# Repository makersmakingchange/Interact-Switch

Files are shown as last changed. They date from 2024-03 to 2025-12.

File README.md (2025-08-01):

 # Interact Switch
<!---  SUMMARY A brief summary of the project. What it does, who it is for, how much it costs. --->

The Interact Switch is an open source assistive switch. The switch is comprised of 3D printed parts and off-the-shelf electronics. The Interact Switch is a high quality, modular 3D printable switch design. The tactile feel of the switch is on par with commercial switches, coming in at about 35 gf of activation force across the surface of the switch. The base has the same footprint as a Jellybean switch, and should work with any Jellybean switch mounts.

There are a wide array of different designs: from a simple flat button, to textured designs, to a dome, and even some wobble switch variants.

The switch base incorporates 6 slots that are ideal for a variety of mounting options, including using hook and loop straps (e.g., VELCRO). The overall cost of materials is about $8 (plus $8 for component shipping).

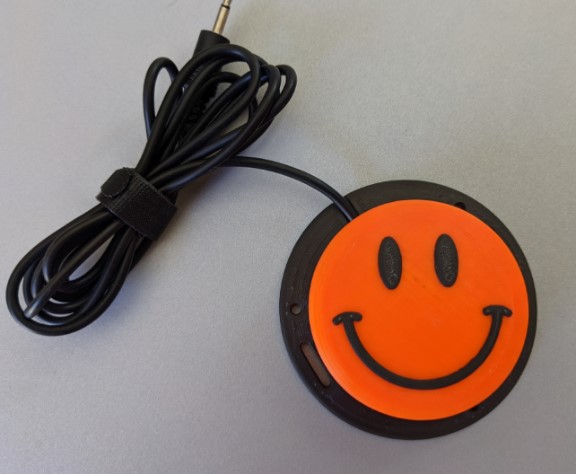
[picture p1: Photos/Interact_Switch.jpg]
A 3D printed Interact Switch with smiley topper


## More info at
- [Makers Making Change Library Page](https://www.makersmakingchange.com/s/product/interact-switch/01tJR000000698vYAA)

## How to Obtain the Device
### 1. Do-it-Yourself (DIY) or Do-it-Together (DIT)

This is an open-source assistive technology, so anyone is free to build it. All of the files and instructions required to build the device are contained within this repository. Refer to the Maker Guide below.

### 2. Request a build of this device

You may also submit a build request through the [MMC Library Page](https://www.makersmakingchange.com/s/product/interact-switch/01tJR000000698vYAA) to have a volunteer maker build the device. As the requestor, you are responsible for reimbursing the maker for the cost of materials and any shipping.

### 3. Build this device for someone else

If you have the skills and equipment to build this device, and would like to donate your time to create the device for someone who needs it, visit the [MMC Maker Wanted](https://makersmakingchange.com/maker-wanted/) section.

## Build Instructions

### 1. Read through the Maker Guide

The Maker Guide  [EN](/Documentation/Interact_Switch_Maker_Guide.pdf), WIP <!---([FR](/Documentation/FR_Interact_Switch_Maker_Guide.pdf)) --->  contains all the necessary information to build this device, including tool lists, assembly instructions, programming instructions (if applicable) and testing.

### 2. Order the Off-The-Shelf Components

The [Bill of Materials](/Documentation/Interact_Switch_BOM.csv) lists all of the parts and components required to build the Interact Switch. The main switch component needs to be ordered online. The rest of the off-the-shelf components are also online or may be available in smaller quantities at your local hardware store or dollar store.

### 3. Print the 3D Printable components

All of the individual print files can be found in the [/Build_Files/3D_Printing_Files](/Build_Files/3D_Printing_Files/) folder.

### 4. Assemble the <Device-Name>

Reference the Assembly Guide([EN](/Documentation/Interact_Switch_Maker_Guide.pdf),[FR](/Documentation/FR_Interact_Switch_Assembly_Guide.pdf)) for the tools and steps required to build each portion.

## How to improve this Device
As open source assistive technology, you are welcomed and encouraged to improve upon the design. 

## Files
### Documentation
| Document             | Version | Link |
|----------------------|---------|------|
| Design Rationale     | 2.0     | [Interact_Switch_Design_Rationale](/Documentation/Interact_Switch_Design_Rationale.pdf)    |
| Maker Guide          | 2.0     | [Interact_Switch_Maker_Checklist](/Documentation/Interact_Switch_Maker_Guide.pdf)          |
| Topper Guide         | 2.0     | [Interact Switch Topper Guide](/Documentation/Interact_Switch_Topper_Guide.pdf)            |
| Bill of Materials    | 2.0     | [Interact_Switch_Bill_of_Materials](/Documentation/Interact_Switch_BOM.csv)                |
| User Guide           | 2.0     | [Interact_Switch_User_Guide](/Documentation/Interact_Switch_Quick_Guide.pdf)               |
| Changelog            | 2.0     | [Interact_Switch_Changelog](CHANGES.txt)     |

### Design Files
<!--- DESIGN FILES If possible, include a copy of original design files to facilitate easy editing and customization. --->
 - [CAD Files](/Design_Files/CAD_Design_Files)

### Build Files
 - [3D Printing Files](/Build_Files/3D_Printing_Files)

## Attribution
The [original design](https://github.com/mwturvey/InteractSwitch) of the Interact Switch was by Mike Turvey.

Modifications to the design and additional documentation by Neil Squire Society / Makers Making Change.
  - Increases the screw hole size in the ButtonCapHolder to accept #4 3/8" screws instead of M2.5 screws.
  - Lines up the holes in the base with the holes in the ButtonCapHolder.
  - Deepens the countersink in the Base for the screws.
  - Removes the need for supports on the Base piece.
  - Decreases the required sanding by tapering the tabs on the ButtonCapHolder.  

Because of the modifications made to the base and button cap holder to accomodate the #4 screws, they are no longer backwards compatible with the original files and is not longer compatible with M2.5 screws.

### Contributors
 - Mike Turvey
 - Stephen Moyer. Neil Squire Society.
 - Brad Wellington. Neil Squire Society.
 - Jake McIvor. Neil Squire Society.
---

<!-- ABOUT MMC START -->
## About Makers Making Change
[Makers Making Change Logo](https://www.makersmakingchange.com/)

Makers Making Change is a program of [Neil Squire](https://www.neilsquire.ca/), a Canadian non-profit that uses technology, knowledge, and passion to empower people with disabilities.

Makers Making Change leverages the capacity of community based Makers, Disability Professionals and Volunteers to develop and deliver affordable Open Source Assistive Technologies.

 - Website: [www.MakersMakingChange.com](https://www.makersmakingchange.com/)
 - GitHub: [makersmakingchange](https://github.com/makersmakingchange)
 - Bluesky: [@makersmakingchange.bsky.social](https://bsky.app/profile/makersmakingchange.bsky.social)
 - Instagram: [@makersmakingchange](https://www.instagram.com/makersmakingchange)
 - Facebook: [makersmakechange](https://www.facebook.com/makersmakechange)
 - LinkedIn: [Neil Squire Society](https://www.linkedin.com/company/neil-squire-society/)
 - Thingiverse: [makersmakingchange](https://www.thingiverse.com/makersmakingchange/about)
 - Printables: [MakersMakingChange](https://www.printables.com/@MakersMakingChange)

### Contact Us
For technical questions, to get involved, or to share your experience we encourage you to [visit our website](https://www.makersmakingchange.com/) or [contact us](https://www.makersmakingchange.com/s/contact).
<!-- ABOUT MMC END -->

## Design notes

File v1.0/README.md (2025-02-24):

Edit: This quick fix to the design incorporates the following:
- Increases the screw hole size in the ButtonCapHolder to accept both M2.5 screws as well as #4 3/8" screws.
- Lines up the holes in the base with the holes in the ButtonCapHolder.
- Deepens the countersink in the Base for the screws.
- Removes the need for supports on the Base piece.
- Decreases the required sanding by tapering the tabs on the ButtonCapHolder.

Note: Only the generic ButtonBase has been updated, not the ButtonBase_Spade.

# InteractSwitch
Designs for a set of assistive technology switches

You can read more about the development of this switch here, as well as see a bunch of pictures & comments: https://cdn.thingiverse.com/assets/da/2f/63/38/8b/card_preview_newButton2.PNG

Build instructions can be found here:

https://docs.google.com/document/d/1uWRKXmApZUaSo1I0oyyFrAfncziYsd2_8ai8dunogJs/edit?usp=sharing

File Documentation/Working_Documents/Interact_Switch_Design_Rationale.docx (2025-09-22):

# Overview

The Design Rationale is intended to provide designers and maker information about the design process and design decisions behind the development of the Interact Switch, a customizable assistive switch with a large activation area.

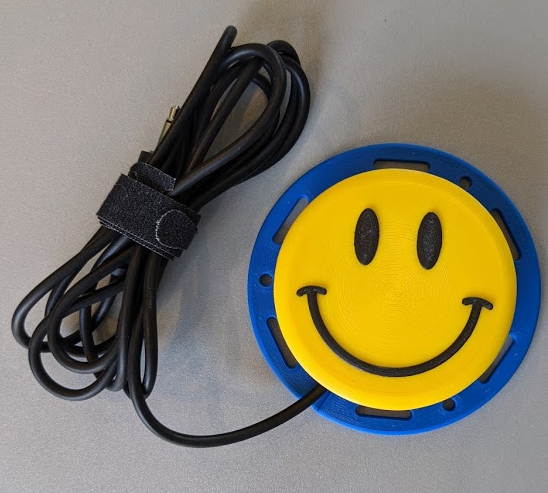
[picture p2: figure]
an interact switch with a smiley face

# Introduction

The original design for the Interact Switch came from the design by Mark Turvey. (https://github.com/mwturvey/InteractSwitch)

# Detailed Design

## Initial Changes

The initial changes made to the original design were

- Increases the screw hole size in the ButtonCapHolder to accept both M2.5 screws as well as #4 3/8" screws.
- Lines up the holes in the base with the holes in the ButtonCapHolder.
- Deepens the countersink in the Base for the screws.
- Removes the need for supports on the Base piece.
- Decreases the required sanding by tapering the tabs on the ButtonCapHolder.

## Improvements over time

Further changes were made over time to the following components

### Base

#### Cable Routing

Changes were made to the cable routing path to make the cable align better to the position of the switch

#### Button Cap

#### Upside Down Print Issues

The filets and arcs on the bottom of the button cap caused print quality issues with bridging when printed upside down. For the textured caps this was not a large issue since it was not printed upside down, but did pose an issue for the plain cap. The arcs and filets were replaced with a straight line to improve the bridging when printed upside down.

### Button Cap Holder

#### Screw Insertion

When assembling the device, some users were having trouble aligning the screw with the holes in the Button Cap Holder, and the screws would sometimes screw into the wall of the holder instead of the hole.

A 0.6mm chamfer was added to the hole to catch and guide the screw into the hole.

#### Screw Torque

When using the #4 sheet metal screw, the torque required to tighten the screw broke some of the holders. The hole was loosened to 3.0mm to get a much better tightening torque, but this makes the base and the cap holder no longer backwards compatible with the original, as it no longer works with M2.5 screws.

## File Update

CAD files were updated and rebuilt into one central file. This corrected several minor errors, such as the screw holes on the base and the screw holes on the cap holder being misaligned by 0.5mm, as well as making heavy use of parameters. Because of this rebuild, changes can be made to one parameter, and the changes will propagate out to all connected parts.

## Soldering Jig

An opportunity for improvement for the Interact Switch that was identified was the creation of a soldering jig to prevent makers from soldering to the wrong terminals on the switch, and to prevent large blobs of solder that would make assembly difficult. After 4 iterations, a soldering jig was created that held the switch at a 90 degree angle to the cable, covers the wrong terminal, and holds the cable in place without tipping.

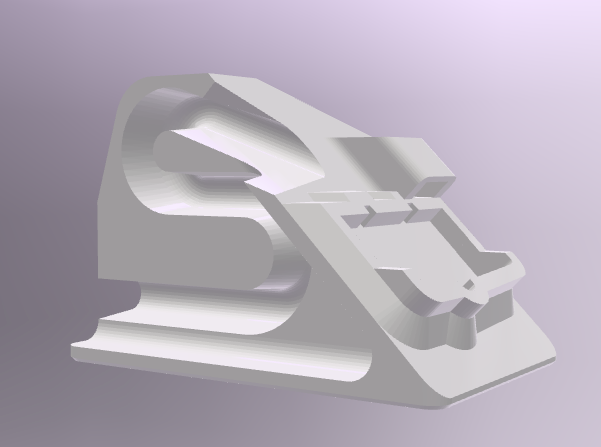
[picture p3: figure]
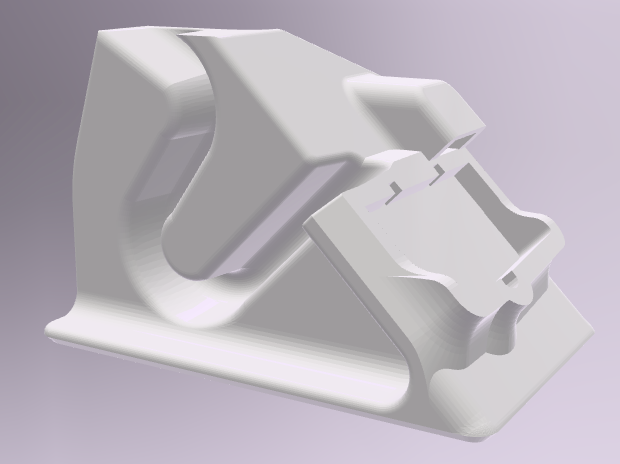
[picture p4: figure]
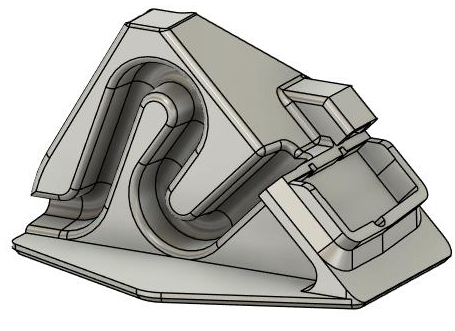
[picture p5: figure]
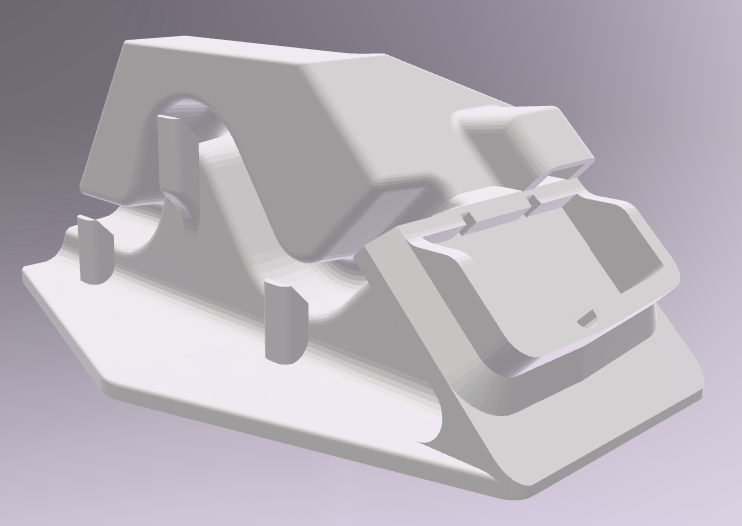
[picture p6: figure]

# Opportunities for Improvement

There are further opportunities for improvement that have been identified

- Better indicate the orientation of the switch when assembling the device
- Clarify how to use the base as a soldering jig
- Change the shape of the button cap for better bridging

© 2025 by Neil Squire. This work is licensed under the CC BY SA 4.0 License: http://creativecommons.org/licenses/by-sa/4.0 Files available at https://github.com/makersmakingchange/Interact-Switch Page 1 of 1

V2.0 | July 2025 Interact Switch Design Rationale

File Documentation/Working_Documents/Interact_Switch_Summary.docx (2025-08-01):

# Overview

The Device Summary is intended to be a detailed summary of the device, product and maker information for the Interact Switch, making it easier to add to the Makers Making Change website. It is intended for anyone who will view the device listing.

an interact switch with a smiley face

# Product Information

## Product Name

Interact Switch

## Device Category

Mark any relevant categories with an “X”:

| Adapted Toys
| Aids for Daily Living (ADL)
X | Assistive Switches
| Communication Aids (AAC)
| Computer Access
| Environmental Controls
| Gaming
| Keyguard
| Kits
| LipSyncs
| Mounting
| Recreation and Leisure
| Seating and Positioning
| Switch Interfaces
| Writing Aids

## User Value Statement

The Interact Switch is a high quality, modular 3D printable switch design. The tactile feel of the switch is on par with commercial switches, coming in at about 35 g of activation force across the surface of the switch. The base has the same footprint as a Jellybean switch, and should work with any Jellybean switch mounts.

## Designer

Original design by Mike Turvey (https://github.com/mwturvey/InteractSwitch)

Modifications to the design and additional documentation by Neil Squire Society / Makers Making Change.

# Device Information

## Overview

The Interact Switch is a high quality, modular 3D printable switch design. The tactile feel of the switch is on par with commercial switches, coming in at about 35 g of activation force across the surface of the switch. The base has the same footprint as a Jellybean switch and should work with any Jellybean switch mounts.

## Disability Type

Select one or more disability types and mark with an “X”:

| Agility / Dexterity
| Arthritis
X | Cognitive
| Hearing
X | Mobility
| Pain
| SCI
| Vision
| Other

## Disability Type Description

## The device is intended for users who have difficulty using small buttons or switches and need an accessible switch to operate them. This switch comes with different topper designs that can be 3D printed in contrasting colors which can be helpful to users with low vision.

## How To Use

The Interact Switch can be connected to any 3.5mm switch-compatible assistive device, such as the Xbox Adaptive Controller. Press the switch to activate the device. Since the device has the same footprint as a Jellybean switch, it is compatible with any Jellybean switch mounts. It can be placed on a flat surface, bolted in place, or secured with hook and loop (ex., Velcro) straps.

## Estimated Cost

The estimated material cost of the device for a single build:

X | $0 - $10
| $11 - $25
| $26 - $50
| $51 - $100
| $101 - $250
| $250+

## Attribution

Original Design by Mike Turvey

# Maker Information

## Project Skills

Mark the required project skills with an “X”:

X | 3D Printing
| Custom PCB
X | Electronics
| Laser Cutting
| Mechanics
| Software
X | Soldering
| Woodworking
| Other

## Skills Description

To build this device a maker needs to be able to 3D print and do basic soldering

## Tools Needed

X | 3D Printer
| Common Hand Tools
| Common Power Tools
| Laser Cutter
X | Soldering Iron
| Specialized Tooling

## Print time (hrs)

1hr8min

## Assembly time (hrs)

0hr10min

## Build Instructions

The parts are 3D printed and assembled with 3 screws. A mono cable is stripped and then soldered to the switch.

## Download Link

https://github.com/makersmakingchange/Interact-Switch/archive/refs/heads/main.zip

## Project Link

https://github.com/makersmakingchange/Interact-Switch

# License

BSD 2-Clause License

Copyright (c) 2020, Michael Turvey

All rights reserved.

Redistribution and use in source and binary forms, with or without

modification, are permitted provided that the following conditions are met:

1. Redistributions of source code must retain the above copyright notice, this

list of conditions and the following disclaimer.

2. Redistributions in binary form must reproduce the above copyright notice,

this list of conditions and the following disclaimer in the documentation

and/or other materials provided with the distribution.

THIS SOFTWARE IS PROVIDED BY THE COPYRIGHT HOLDERS AND CONTRIBUTORS "AS IS"

AND ANY EXPRESS OR IMPLIED WARRANTIES, INCLUDING, BUT NOT LIMITED TO, THE

IMPLIED WARRANTIES OF MERCHANTABILITY AND FITNESS FOR A PARTICULAR PURPOSE ARE

DISCLAIMED. IN NO EVENT SHALL THE COPYRIGHT HOLDER OR CONTRIBUTORS BE LIABLE

FOR ANY DIRECT, INDIRECT, INCIDENTAL, SPECIAL, EXEMPLARY, OR CONSEQUENTIAL

DAMAGES (INCLUDING, BUT NOT LIMITED TO, PROCUREMENT OF SUBSTITUTE GOODS OR

SERVICES; LOSS OF USE, DATA, OR PROFITS; OR BUSINESS INTERRUPTION) HOWEVER

CAUSED AND ON ANY THEORY OF LIABILITY, WHETHER IN CONTRACT, STRICT LIABILITY,

OR TORT (INCLUDING NEGLIGENCE OR OTHERWISE) ARISING IN ANY WAY OUT OF THE USE

OF THIS SOFTWARE, EVEN IF ADVISED OF THE POSSIBILITY OF SUCH DAMAGE.

© 2025 by Neil Squire. This work is licensed under the CC BY SA 4.0 License: http://creativecommons.org/licenses/by-sa/4.0 Page 1 of 2

V2.0 | July 2025 Interact Switch Summary

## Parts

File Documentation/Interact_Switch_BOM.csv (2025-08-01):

Device: | Interact Switch
Version: | V2.0
Last Updated: | 2025-07-08
 |  |  |  |  |  |  |  | Total filament (g) |  | Unit Cost | Total Estimated Cost | Build Cost
 |  |  |  |  |  |  |  | 35 |  | $8.70 | $8.70
ID | Commercial Parts |  |  |  |  |  |  |  |  | $7.82 | $7.82
 | Part | Description |  | Manufacturer | Supplier | QTY / Device | QTY / PKG | PKGs | $/ PKG | $ / Device | Total Estimated Cost |  | Link
 | Mono Cable |  |  |  | Digikey | 1 | 1 | 1 | $4.65 | $4.65 | $4.65 |  | https://www.digikey.ca/en/products/detail/tensility-international-corp/10-00344/2350247
 | Snap Action Switch |  |  |  | Digikey | 1 | 1 | 1 | $1.40 | $1.40 | $1.40 |  | https://www.digikey.ca/en/products/detail/omron-electronics-inc-emc-div/SS-3GP/664724
 | #4 Sheet Metal Screw |  |  |  | Digikey | 3 | 1 | 3 | $0.59 | $1.77 | $1.77 |  | https://www.digikey.ca/en/products/detail/serpac/6005/307599
 |  |  |  |  |  |  |  | 0 |  | $- | $-
 |  |  |  |  |  |  |  | 0 |  | $- | $-
 | 3D Printed Parts |  |  |  |  |  |  | 35 |  | $0.88 | $0.88
 | Part | Description | Filament Type | Filament | Color | QTY / Device | Mass (g) / Part | Total Mass | $ / kg | $ / Device | Total Estimated Cost |  | Link
 | Interact_Switch_Base |  | PLA |  | Any | 1 | 17 | 17 | $25.00 | $0.43 | $0.43
 | Interact_Switch_Cap_Plain |  | PLA |  | Any | 1 | 14 | 14 | $25.00 | $0.35 | $0.35
 | Interact_Switch_Holder |  | PLA |  | Any | 1 | 3 | 3 | $25.00 | $0.08 | $0.08
 | Interact_Switch_Insert_0.6mm |  | PLA |  | Any | 1 | 1 | 1 | $25.00 | $0.03 | $0.03
 |  |  |  |  |  |  |  | 0 |  | $- | $-
 |  |  |  |  |  |  |  | 0 |  | $- | $-
 |  |  |  |  |  |  |  | 0 |  | $- | $-
 |  |  |  |  |  |  |  | 0 |  | $- | $-

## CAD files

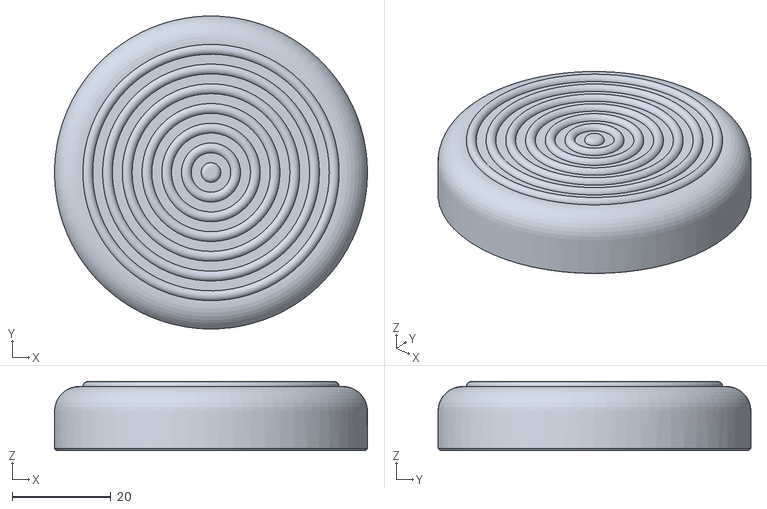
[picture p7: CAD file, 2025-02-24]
Build_Files/3D_Printing_Files/Alternate_Caps/ButtonCap_Rings.STL
63.5 x 63.5 x 14.0

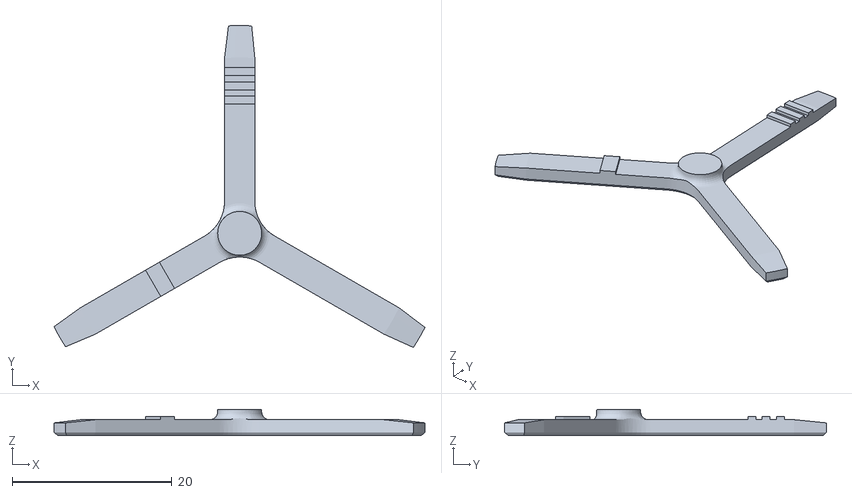
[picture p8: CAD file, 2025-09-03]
Build_Files/3D_Printing_Files/Alternate_Inserts/ButtonCapInsert_1.3mm.STL
46.4 x 40.3 x 3.30

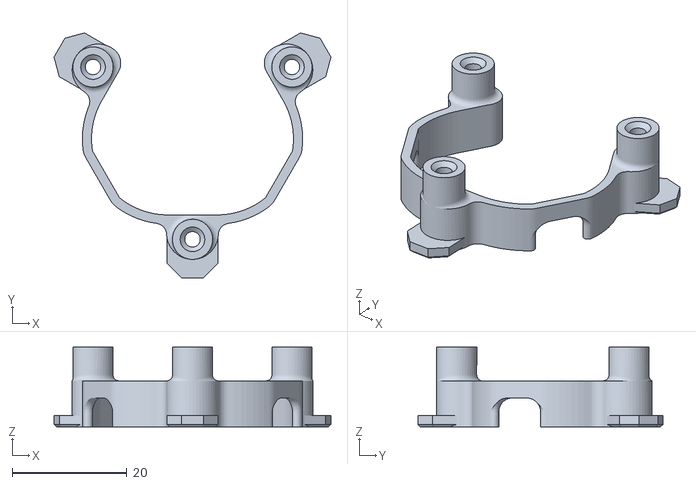
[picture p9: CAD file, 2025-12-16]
Build_Files/3D_Printing_Files/Interact_Switch_Holder.stl
48.2 x 42.7 x 13.9

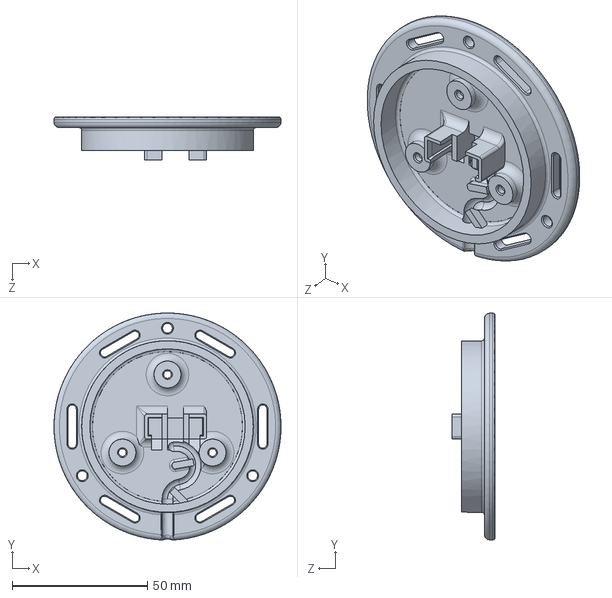
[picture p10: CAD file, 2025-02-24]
v1.0/sources/Base/ButtonBase_Spade.SLDPRT
84.0 x 84.0 x 16.0 mm

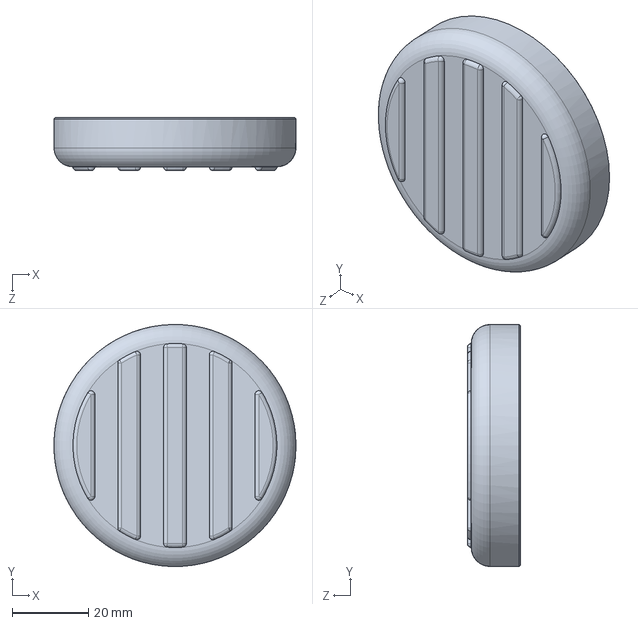
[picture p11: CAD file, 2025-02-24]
v1.0/sources/ButtonCap/ButtonCap_Lines_VeryWide.SLDPRT
63.5 x 63.5 x 14.0 mm

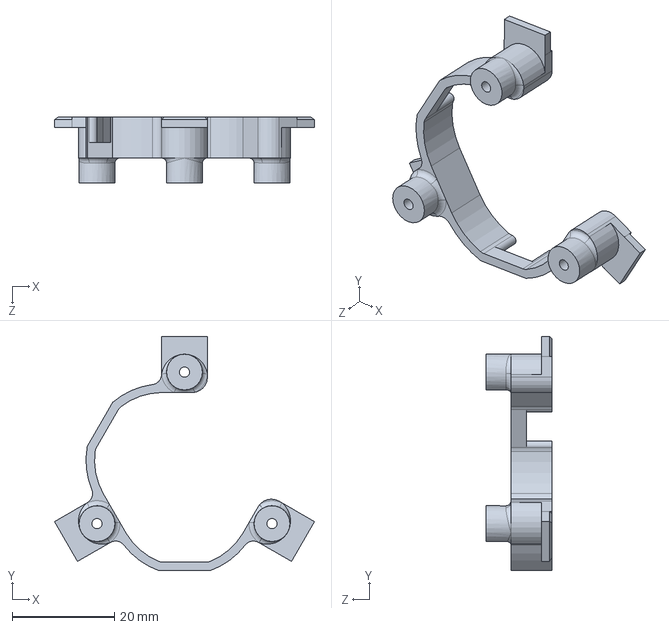
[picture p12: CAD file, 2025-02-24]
v1.0/sources/ButtonCapHolder/ButtonCapHolder.SLDPRT
50.8 x 45.8 x 12.8 mm

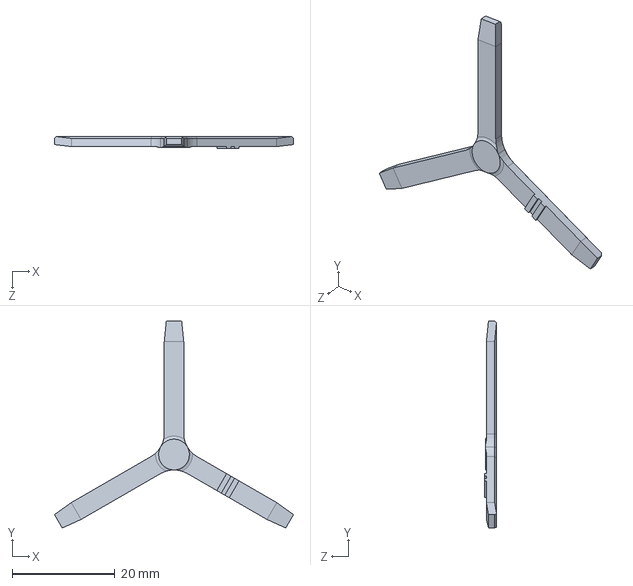
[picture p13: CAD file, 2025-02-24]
v1.0/sources/ButtonCapInsert/ButtonCapInsert_0.2mm.SLDPRT
46.5 x 40.3 x 2.40 mm

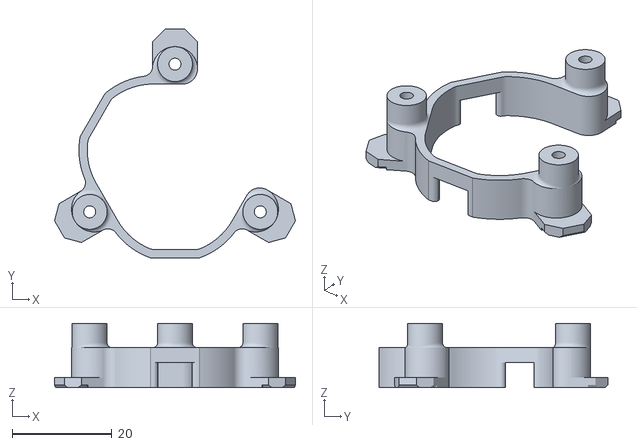
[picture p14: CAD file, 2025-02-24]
v1.0/stl/ButtonCapHolder/Quick Fix ButtonCapHolder.stl
48.3 x 45.8 x 12.9

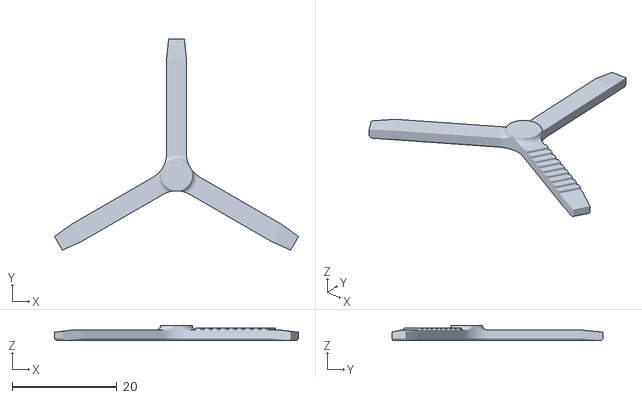
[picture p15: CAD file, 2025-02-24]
v1.0/stl/ButtonCapInsert/ButtonCapInsert_0.9mm.STL
46.5 x 40.3 x 2.90

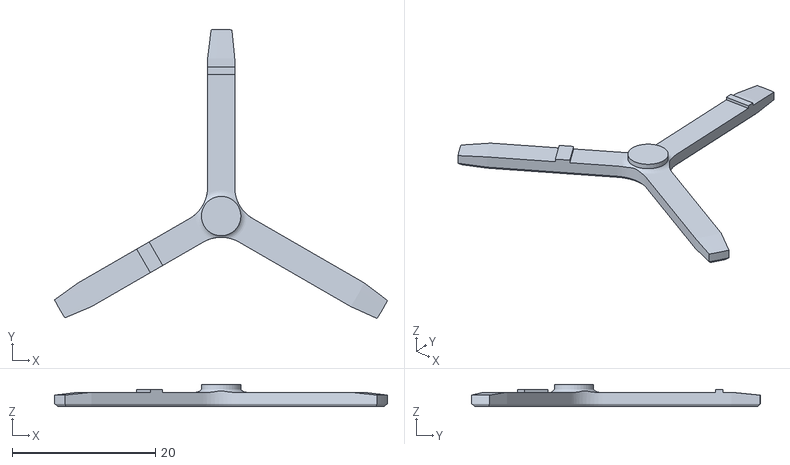
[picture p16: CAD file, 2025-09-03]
Build_Files/3D_Printing_Files/Alternate_Inserts/ButtonCapInsert_1.1mm.STL
46.4 x 40.3 x 3.10

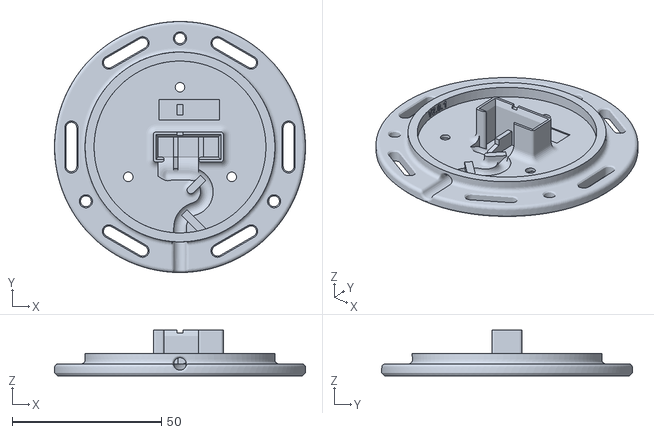
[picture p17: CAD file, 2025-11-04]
Build_Files/3D_Printing_Files/Interact_Switch_Base.stl
84.0 x 84.0 x 15.3

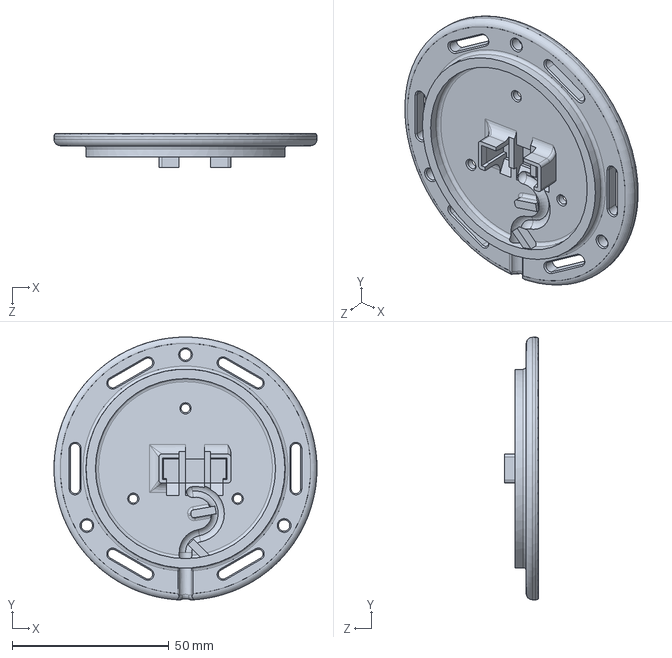
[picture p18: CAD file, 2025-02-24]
v1.0/sources/Base/ButtonBase.SLDPRT
84.0 x 84.0 x 11.0 mm

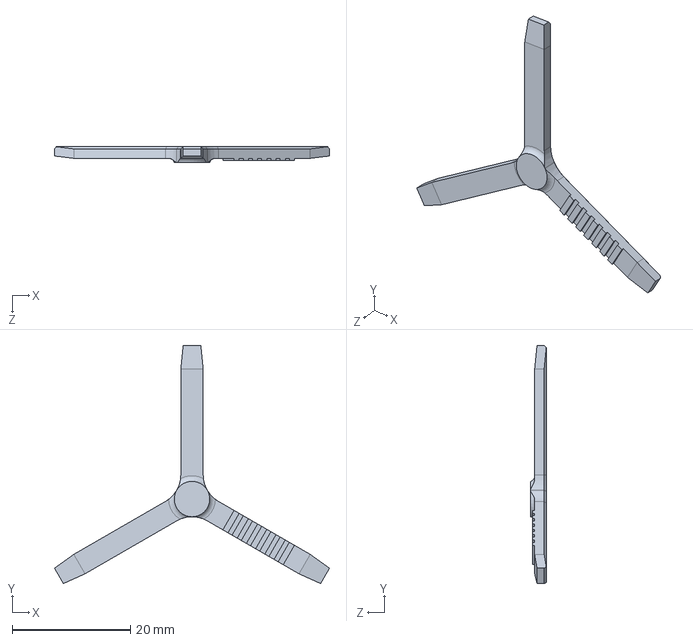
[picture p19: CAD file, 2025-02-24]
v1.0/sources/ButtonCapInsert/ButtonCapInsert_0.7mm.SLDPRT
46.5 x 40.3 x 2.70 mm

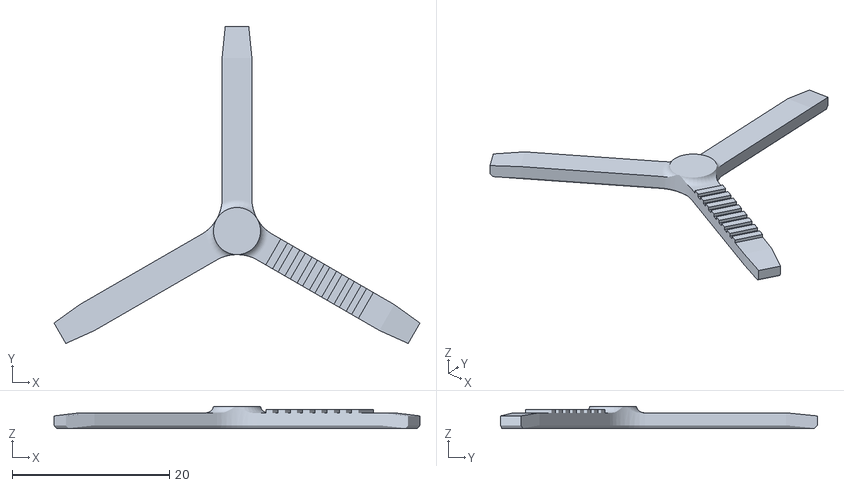
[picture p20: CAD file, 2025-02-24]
v1.0/stl/ButtonCapInsert/ButtonCapInsert_0.8mm.STL
46.5 x 40.3 x 2.80

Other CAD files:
v1.0/stl/Base/ButtonBase_Spade.STL
Build_Files/3D_Printing_Files/Alternate_Caps/ButtonCap_Lines_VeryWide.STL
v1.0/sources/ButtonCap/ButtonCap_Lines_Wide.SLDPRT
v1.0/stl/Base/Quick Fix ButtonBase.stl
Build_Files/3D_Printing_Files/Alternate_Caps/ButtonCap_Arrow.STL
Build_Files/3D_Printing_Files/Alternate_Caps/ButtonCap_Circle.STL
Build_Files/3D_Printing_Files/Alternate_Caps/ButtonCap_Dome.STL
Build_Files/3D_Printing_Files/Alternate_Caps/ButtonCap_Dots_Circles.STL
Build_Files/3D_Printing_Files/Alternate_Caps/ButtonCap_Dots_Wide.STL
Build_Files/3D_Printing_Files/Alternate_Caps/ButtonCap_Lines.STL
Build_Files/3D_Printing_Files/Alternate_Caps/ButtonCap_Lines_Wide.STL
Build_Files/3D_Printing_Files/Alternate_Caps/ButtonCap_Octagon.STL
Build_Files/3D_Printing_Files/Alternate_Caps/ButtonCap_Plain.STL
Build_Files/3D_Printing_Files/Alternate_Caps/ButtonCap_Rings_Wide.STL
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

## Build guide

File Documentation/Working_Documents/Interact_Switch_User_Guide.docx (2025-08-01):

## Introduction

The Interact Switch is a highly customizable switch with a large activation area.

## Features

an interact switch with a smiley face

Switch Surface

Cable

Mounting Slots

## Specifications

Item | Interact Switch
Size (Length x Width x Height) [mm] | 85x85x30
Mass [g] | 60
Press Force [g] | 35

## Compatibility

The Interact Switch is compatible with any accessible device that uses a standard 3.5mm mono jack switch.

## Usage

### Initial Setup

Place the Interact Switch where it works best for the user. Hook and loop fastener (e.g., VELCRO) or a non-slip mat (e.g., DYCEM) can be used to prevent it from sliding on a surface, and the holes and slots around the rim can be used to screw, cable tie, or otherwise fasten it into place.

### Regular Use

When the Interact Switch is connected to the device, a press of the switch will register as a button press on the connected port.

### Takedown / Storage

When not in use, the Interact Switch should be stored in a cool place out of direct sunlight.

## Care

The Interact Switch is made of 3D printed plastic. Exposure to high heat may cause warping and/or negatively affect function. Extended exposure to sunlight will also weaken the plastic on the device.

The Interact Switch contains electronics and is not waterproof. If the device becomes wet, make sure it is off and do not use it until it has completely dried. It may help to open any electronic enclosures to speed up drying and ensure it has completely dried.

### Cleaning

The Interact Switch can be wiped with a damp cloth. The Interact Switch can also be cleaned by scrubbing with warm water and dish soap, but should not be submerged in water. Do not use hot water or clean in a dishwasher.

## Disposal

PLA filament may be industrially compostable in your area. Check with your waste management company if PLA can be composted or must be thrown in the garbage.

Disassemble the Interact Switch and separate out the recyclable and compostable components, and those that must be thrown out. Electronics and batteries should be disposed of following your local waste management guidelines.

© 2025 by Neil Squire. This work is licensed under the CC BY SA 4.0 License: http://creativecommons.org/licenses/by-sa/4.0 Files available at https://github.com/makersmakingchange/Interact-Switch Page 2 of 3

V2.0 | July 2025 Interact Switch user Guide

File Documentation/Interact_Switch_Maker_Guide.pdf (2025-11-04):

V2.0 | July 2025

## Interact Switch

## MAKER GUIDE

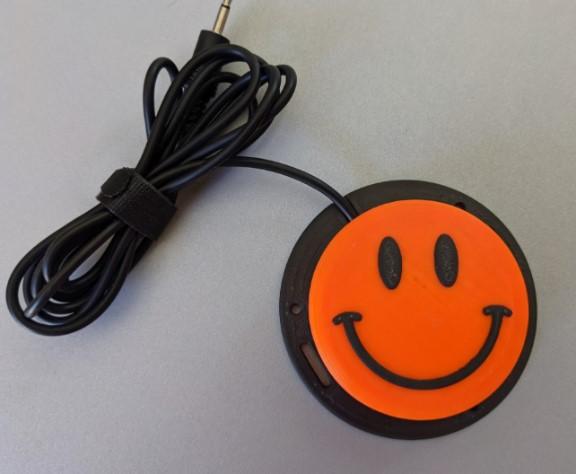
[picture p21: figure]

© 2025 by Neil Squire. (https://neilsquire.ca/)
This work is licensed under the CC BY SA 4.0 License: http://creativecommons.org/licenses/by-sa/4.0
Files available at https://github.com/makersmakingchange/Interact-Switch | Page 1 of 14

### Overview

This document contains the necessary information to build the Interact Switch, a large customizable switch with a low activation force.

## MAKER GUIDE

Files available at https://github.com/makersmakingchange/Interact-Switch | Page 2 of 14

### Contents

Overview | 1
Maker Checklist | 3
Maker To Do List | 3
Items to Give to User | 3
Attribution | 3
Tool List | 4
Tools / Equipment | 4
Supplies | 4
Personal Protective Equipment (PPE) | 4
Customization Guide | 5
3D Printing Guide | 7
3D Printing Summary | 7
3D Printing Settings | 7
Post-Processing | 8
Examples of Quality Prints | 8
Building the Interact Switch | 9
Required Components | 9
Required Tools and Supplies | 9
Required Personal Protective Equipment (PPE) | 9
Assembly Steps | 10
Testing | 14
Troubleshooting | 14

## MAKER GUIDE

Files available at https://github.com/makersmakingchange/Interact-Switch | Page 3 of 14

### Maker Checklist

This list provides an overview of the steps required to build and deliver the Interact Switch.

### Maker To Do List

Read through the Maker Guide to become familiar with required components, tools, supplies, safety gear, and overall assembly steps.
Talk to the User about customization options
- What colour(s) would they like the topper and/or topper pattern to be printed in?
- Which topper would they like to have? There are a variety of toppers available with different patterns and textures.
- How would they like to receive the “User Guide”? (PDF or physical copy)
Order hardware components
Gather tools, supplies, and safety equipment.
Assemble the device
Test the Interact Switch

### Items to Give to User

Interact Switch
User Guide

### Attribution

The Interact Switch (https://github.com/mwturvey/InteractSwitch/tree/master) design by Mike Turvey (https://github.com/mwturvey) is used under CC-BY 4.0. (https://creativecommons.org/licenses/by/4.0/) Instructions adapted from Original Interact Switch Assembly Instructions (https://docs.google.com/document/d/1uWRKXmApZUaSo1I0oyyFrAfncziYsd2_8ai8dunogJs/edit?usp=sharing) by Mike Turvey, (https://github.com/mwturvey) used under CC-BY 4.0. (https://creativecommons.org/licenses/by/4.0/)

Due to changes made to make the switch compatible with the #4 sheet metal screws, the Base and Switch holder are no longer compatible with the original parts.

## MAKER GUIDE

Files available at https://github.com/makersmakingchange/Interact-Switch | Page 4 of 14

### Tool List

### Tools / Equipment

Tool ID | Description | Required / Recommended | Notes
T01 | Wire Strippers | Required | Stripping insulation from the cable
T02 | Soldering Iron | Required | Soldering the Cable to the switch
T03 | Phillips Screwdriver | Required | Attaching the base to the top

### Supplies

Supplies ID Description | Quantity | Notes
S01 | Solder | Roughly 1 inch | To attach the mono cable to the button

### Personal Protective Equipment (PPE)

PPE ID | Description | Notes
P01 | Safety Glasses | To keep flying debris out of your eyes

## MAKER GUIDE

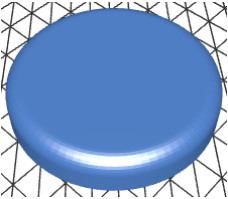
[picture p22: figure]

Files available at https://github.com/makersmakingchange/Interact-Switch | Page 5 of 14

### Customization Guide

The device can be printed in the user’s desired colour.

There are over 12 different button caps available in the GitHub repository, and some projects such as the Open Playback Recorder have custom Interact Switch caps that match buttons on the device.

When printing the textured button caps, a filament change can be done to print the textured part of the cap in a different colour from the main body, increasing contrast. This can also be done automatically on printers that support multi-material printing.

The plain, ‘default’ button topper can be seen below, and the other options included in the Interact Switch Repository are listed in the table below.

## MAKER GUIDE

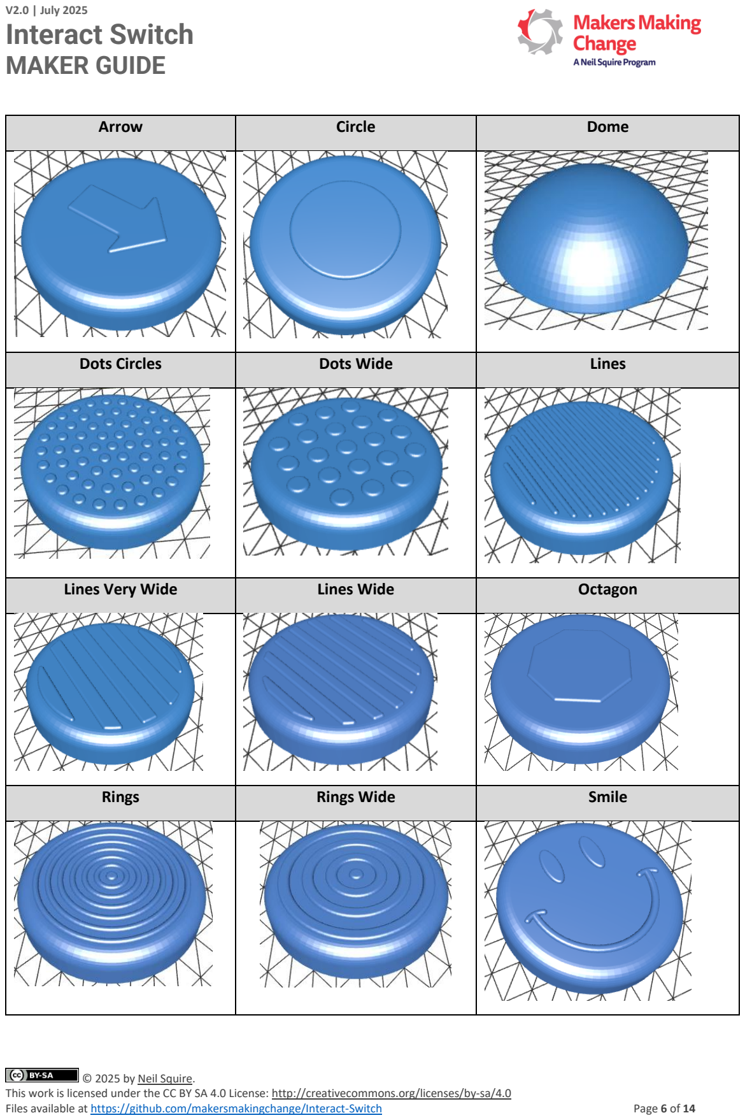
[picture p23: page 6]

Files available at https://github.com/makersmakingchange/Interact-Switch | Page 6 of 14
Arrow | Circle | Dome
Dots Circles | Dots Wide | Lines
Lines Very Wide | Lines Wide | Octagon
Rings | Rings Wide | Smile

## MAKER GUIDE

Files available at https://github.com/makersmakingchange/Interact-Switch | Page 7 of 14

### 3D Printing Guide

The device was originally printed on a Bambu P1S using Bambu Studio using the default profile.

### 3D Printing Summary

Metrics | Single Unit
Total Print Time (hour min) | 1h8min
Total Number of Components | 4
Typical Total Mass (g) | 35
Typical Number of Print Setups | 3

### 3D Printing Settings

Note that the 3D printing material should be assumed to be PLA unless otherwise noted in the table below.

Print File Name | Qty | Total Print Time (hr:min) | Mass (g) | Infill (%) | Suppor (Y/N) | Layer Height/ Nozzle Diameter(mm) | Notes
Interact_Switch_Base.stl | 1 | 0:32 | 17 | 20 | N | 0.2/0.4
Interact_Switch_Cap_Plain.stl | 1 | 0:25 | 14 | 20 | N | 0.2/0.4 | Default cap; others are available
Interact_Switch_Holder.stl | 1 | 0:09 | 3 | 20 | N | 0.2/0.4
Interact_Switch_Insert_0.6mm.stl | 1 | 0:02 | 1 | 20 | N | 0.1/0.4 | Print with 0.1 mm layer height if printing an odd numbered insert (i.e. a 0.5 mm or 0.9 mm)
Interact_Switch_Solder_Jig.stl | 1 | 0:25 | 12 | 20 | N | 0.2/0.4 | Optional

Depending on the tolerances of your printer, you may have to print a different switch insert than the
0.6mm insert. The insert is the part that makes the cap press the switch in the base, and depending on the tolerances of your printer, this distance might be too close or too far for the 0.6mm insert. The repository includes inserts from 0.2 to 1.5mm and it may take a few tries to find the right one that works for your printer.

## MAKER GUIDE

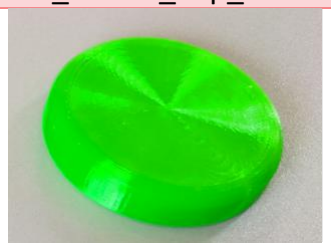
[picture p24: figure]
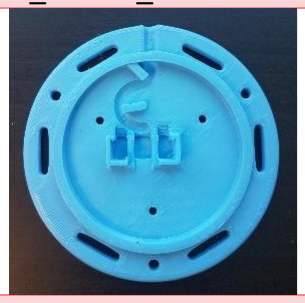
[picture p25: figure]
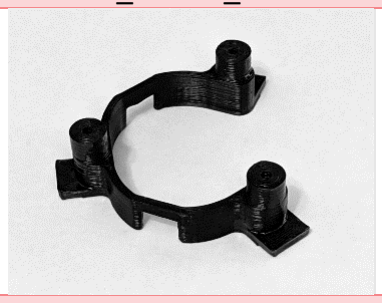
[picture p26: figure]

Files available at https://github.com/makersmakingchange/Interact-Switch | Page 8 of 14

### Post-Processing

Inspect the 3D printed parts for any printing defects, sharp edges, or burrs. Sharp edges and burrs can be removed with sanding or deburring tools.

### Examples of Quality Prints

Compare your 3D prints to the images here. If there are significant differences, you may need to reprint the part.

Interact Switch
Interact_Switch_Base.stl | Interact_Switch_Cap_Plain.stl | Interact_Switch_Holder.stl

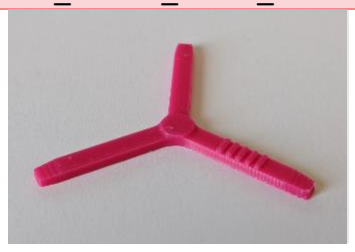
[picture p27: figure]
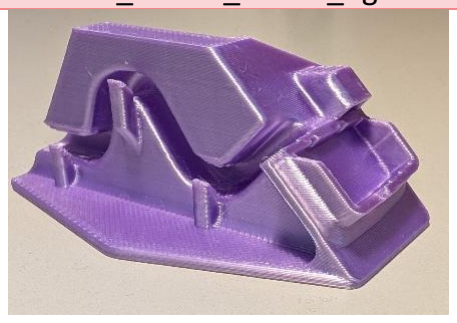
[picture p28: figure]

Interact_Switch_Insert_0.6mm.stl | Interact_Switch_Solder_Jig.stl

## MAKER GUIDE

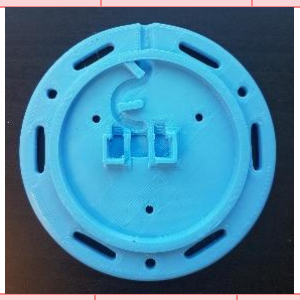
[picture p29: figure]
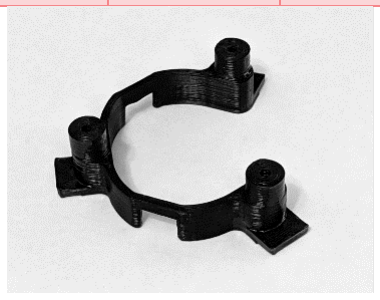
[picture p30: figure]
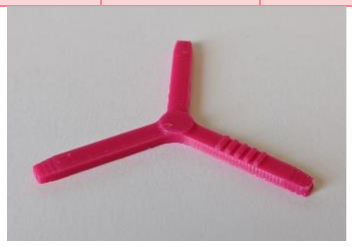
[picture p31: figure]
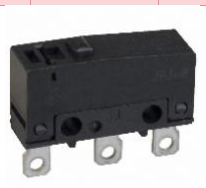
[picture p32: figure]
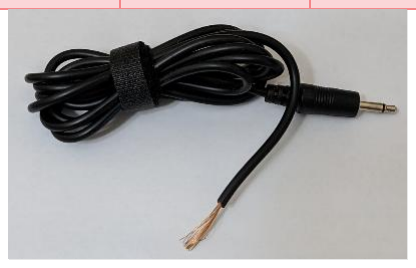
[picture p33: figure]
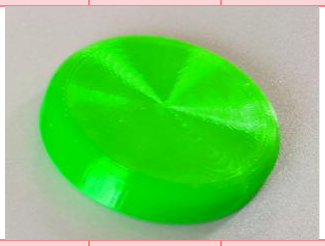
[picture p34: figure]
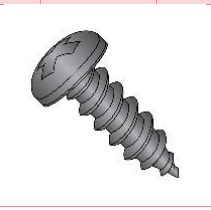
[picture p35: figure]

Files available at https://github.com/makersmakingchange/Interact-Switch | Page 9 of 14

### Building the Interact Switch

Required Components
Interact Switch
A01 | Switch Base | QTY: 1 | A02 | Button Cap Holder
QTY: 1 | A03 | Button Cap
Insert

QTY: 1

A04 | Button Cap | QTY: 1 | A05 | Limit Switch
QTY: 1 | A06 | Mono
Cable

QTY: 1

A07 #4 Sheet Metal Screw

QTY: 3

Required Tools and Supplies
- Wire Strippers
- Soldering Iron
- Screwdriver

Required Personal Protective Equipment (PPE)
- Safety Glasses

## MAKER GUIDE

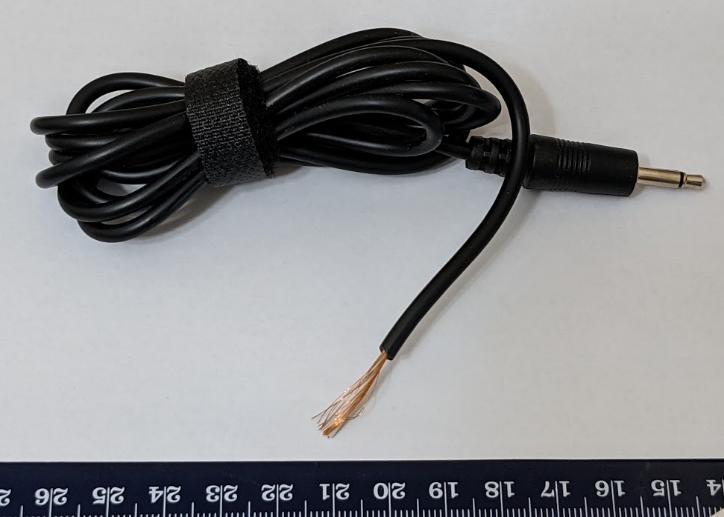
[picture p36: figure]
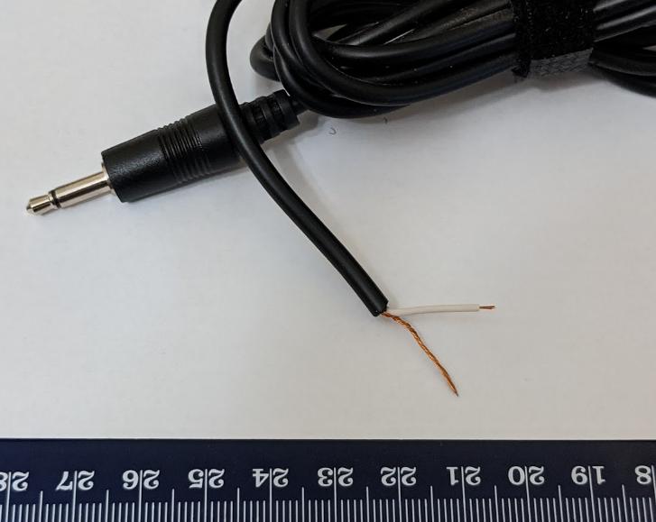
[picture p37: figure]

Files available at https://github.com/makersmakingchange/Interact-Switch | Page 10 of 14

Assembly Steps

Step 1: Prep Cable
Cut off and discard one of the plugs from the mono audio cable.

Use the wire strippers to carefully remove about 15 mm of the outer insulation from the end.

Step 2: Prep Cable Wires
Twist the copper strands together into a single wire.

Use the wire strippers to remove roughly 5 mm of insulation from the other wire.

(Note: Your cable may differ. If there are two wires with insulation, strip 5 mm from the end of each wire.)

## MAKER GUIDE

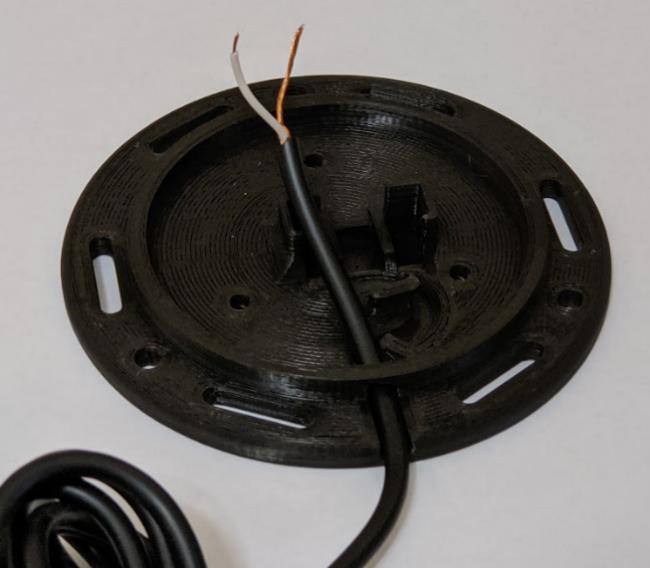
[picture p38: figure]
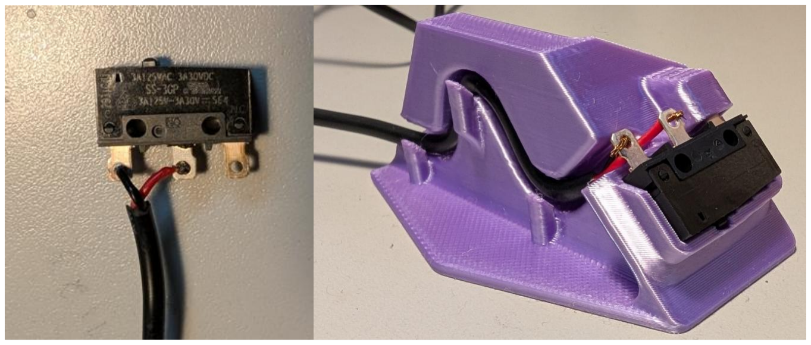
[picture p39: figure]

Files available at https://github.com/makersmakingchange/Interact-Switch | Page 11 of 14
Step 3: Thread Cable into Switch Base
Thread the cable through the hole in the Switch Base. You will not be able to do this after you solder the limit switch onto the wire.
Step 4: Solder Wires to Switch
Solder the wires into the switch in the position shown below. The optional soldering jig can be used to hold the cable and switch in place, and to isolate the correct terminals to solder to.

Note: Solder the two leads closest to the button on the switch.

Test: plug your switch into a switch activated device and push the button on the limit switch

## MAKER GUIDE

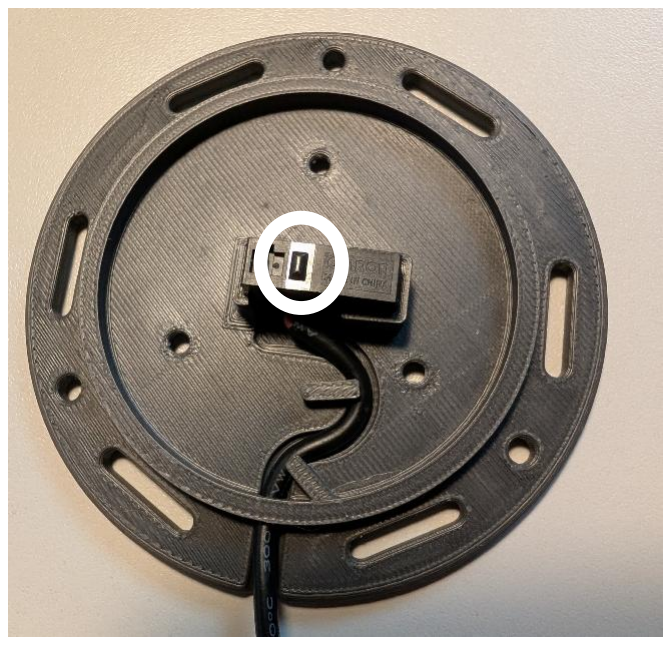
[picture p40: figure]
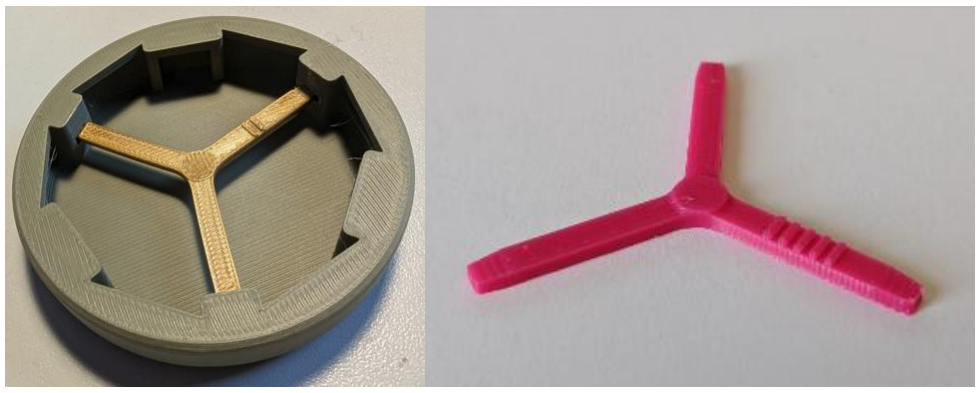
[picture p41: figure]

Files available at https://github.com/makersmakingchange/Interact-Switch | Page 12 of 14
Step 5: Position Switch in Base
Place the limit switch into the Switch Base as shown.

For the orientation of the switch, when the cable is coming towards you, the button on the limit switch should be offset to the left. Make sure that no wires are stuck underneath, preventing the limit switch from going all the way down.

Push the cable in the slot as shown in the picture.

Step 6: Assemble Button Cap
Turn the Button Cap over and insert the Button Cap Insert. If you’re unsure which size to use, try starting with 0.6 mm. The lines on the button insert should be facing up, with the print surface facing down towards the cap. The raised section where all three legs on the insert join should be visible.

## MAKER GUIDE

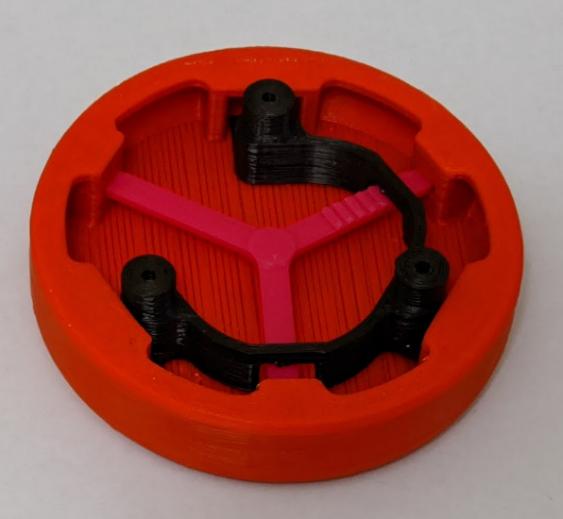
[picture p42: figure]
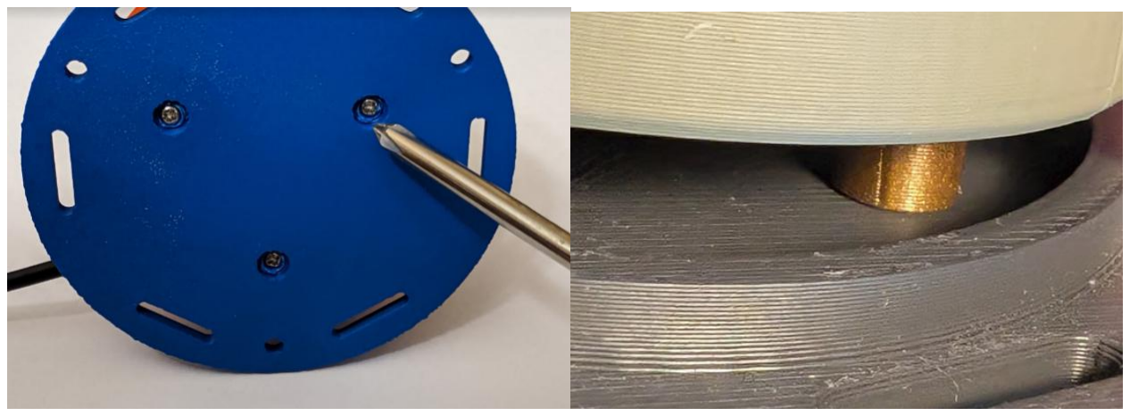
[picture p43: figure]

Files available at https://github.com/makersmakingchange/Interact-Switch | Page 13 of 14
Step 7: Finalize Button Cap Assembly
Insert the Button Cap Holder into the Button Cap Assembly. The orientation of the “open” side doesn’t matter.

Note: for smoother switch action, sand the edges of the Button Cap Holder where it rubs on the switch.

Step 8: Assemble Switch
Align the three posts of the Switch Cap Holder to the three holes in the Switch Base. Secure the Switch Cap Holder to the Switch Base using three screws. Tighten them until the Switch Cap holder is firmly against the base.

Note: Be careful not to over tighten the screws. Tighten them until you notice the resistance increases and the Switch Cap Holder is firmly against the Switch Base.

## MAKER GUIDE

Files available at https://github.com/makersmakingchange/Interact-Switch | Page 14 of 14

### Testing

The last thing to do is test your switch. If this is your first switch, you’ll likely need to test it out and figure out the best size of Switch Cap Insert to use.

The first thing to do to test a switch is to push it a lot. Tap it everywhere, repeatedly. Every time you push it, you should hear it click down and click as it goes back up. It should never stick. If you wiggle the top, it should move some, but it shouldn’t feel like it’s rattling around. Next, plug the switch into a switch activated device and make sure that it works.

### Troubleshooting

Problem | Solution
The switch cap is too loose and rattles around easily. | Use a larger/ thicker Switch Cap Insert.
Switch doesn’t make any noise when pushed. | Use a smaller/ thinner Switch Cap Insert. An insert that is too big can cause the limit switch to be always depressed. When this is the case, you’ll often hear the limit switch “click” closed when you’re screwing everything together, but it won’t ever click open.
Switch sticks/ doesn’t always go back up. | Use a smaller/ thinner Switch Cap Insert. You may likely need just one size thinner.
Switch makes clicking noise, but the switch activated device isn’t activating | • Test the switch activated device with a switch known to work, just to make sure it’s working fine. • Check that the plug is firmly plugged into the device • The solder connection may be bad and need to be re-soldered. • There may be an internal break in the wire, and you will need to replace it. This is a particularly common failure point for an older switch.

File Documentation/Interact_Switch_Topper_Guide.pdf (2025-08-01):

V2.0 | July 2025

## Interact Switch

## TOPPER GUIDE

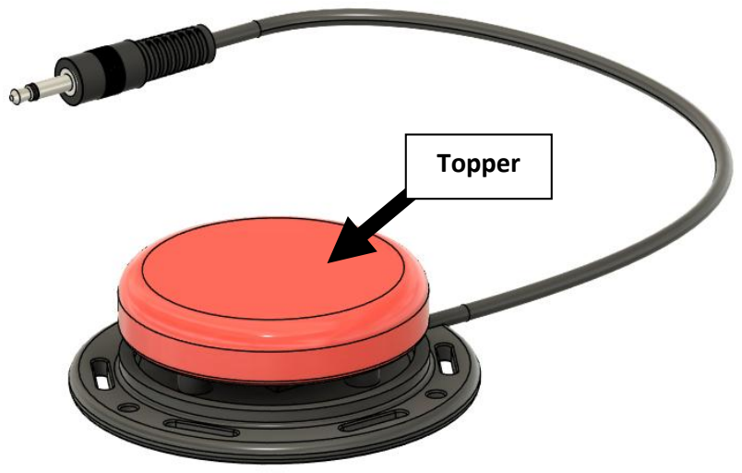
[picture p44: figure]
Topper

© 2025 by Neil Squire. (https://neilsquire.ca/)

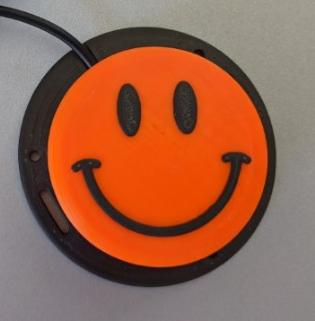
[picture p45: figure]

This work is licensed under the CC BY SA 4.0 License: http://creativecommons.org/licenses/by-sa/4.0
Files available at https://github.com/makersmakingchange/Interact-Switch | Page 1 of 2

### Overview

The Interact Switch is available with several different Switch Tops. Using different colors and textures can help a user distinguish between switches by sight or feel. The plain, ‘default’ button topper can be seen below, and the other options included in the Interact Switch Repository are listed in the table on the next page.

Generally, it is also possible and easy to print toppers in different colors. It is also possible to print a topper in multiple colors based on the height. This is illustrated below with a Smile Topper that has the main portion printed in orange and the raised portion printed in black.

## Interact Switch

## TOPPER GUIDE

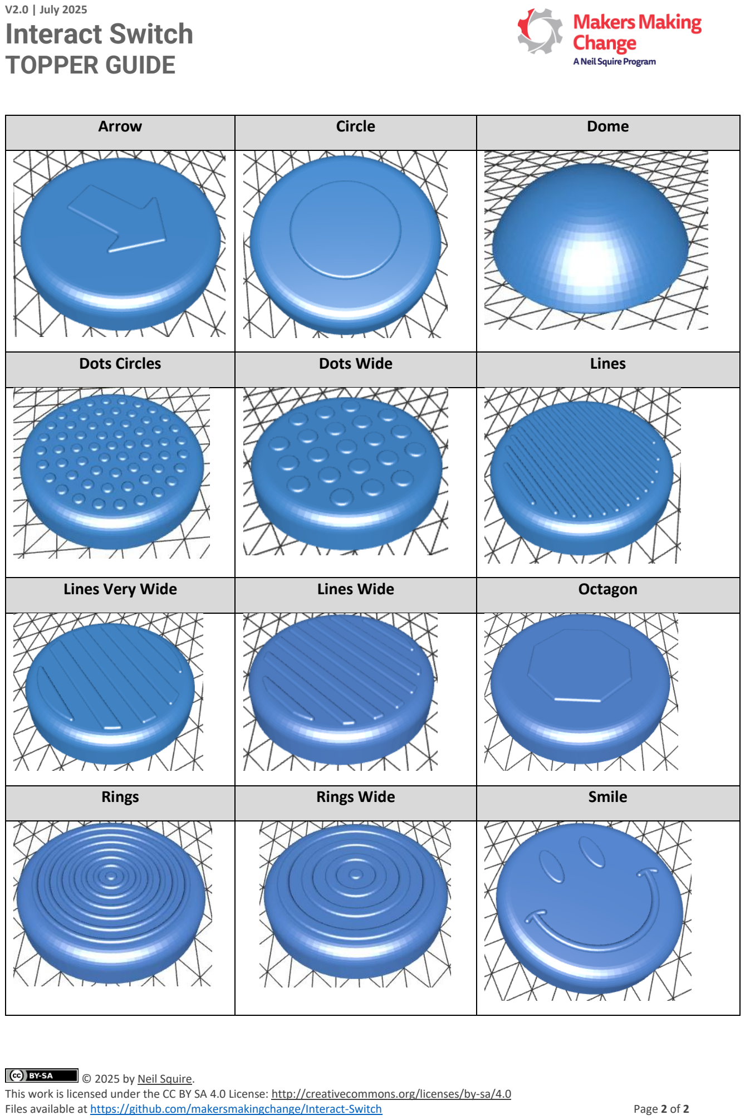
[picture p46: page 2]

V2.0 | July 2025

© 2025 by Neil Squire. (https://neilsquire.ca/)
This work is licensed under the CC BY SA 4.0 License: http://creativecommons.org/licenses/by-sa/4.0
Files available at https://github.com/makersmakingchange/Interact-Switch | Page 2 of 2
Arrow | Circle | Dome
Dots Circles | Dots Wide | Lines
Lines Very Wide | Lines Wide | Octagon
Rings | Rings Wide | Smile

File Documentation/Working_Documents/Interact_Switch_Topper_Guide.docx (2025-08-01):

# Overview

The Interact Switch is available with several different Switch Tops. Using different colors and textures can help a user distinguish between switches by sight or feel. The plain, ‘default’ button topper can be seen below, and the other options included in the Interact Switch Repository are listed in the table on the next page.

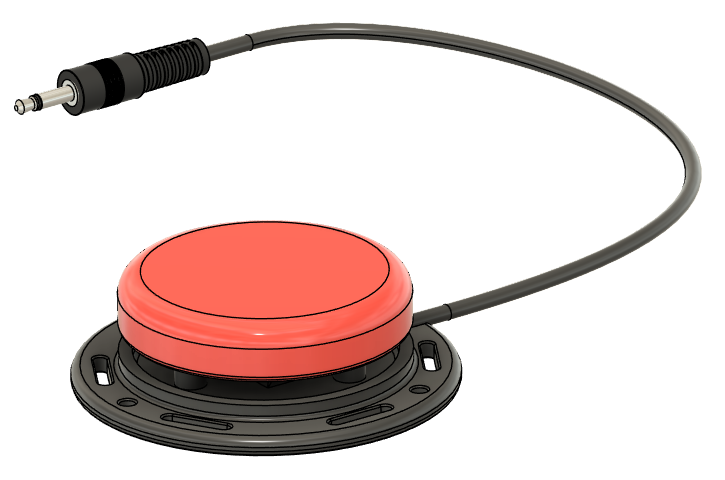
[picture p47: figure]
An Interact Switch with a plain red topper and a black base

Topper

Generally, it is also possible and easy to print toppers in different colors. It is also possible to print a topper in multiple colors based on the height. This is illustrated below with a Smile Topper that has the main portion printed in orange and the raised portion printed in black.

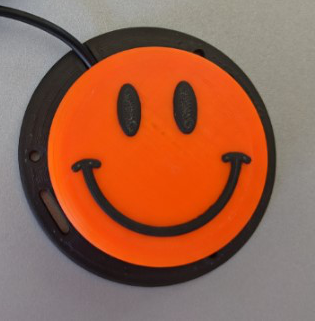
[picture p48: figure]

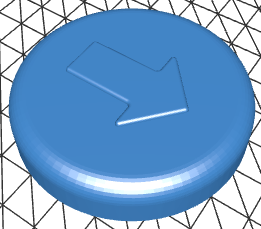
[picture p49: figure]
3D render of arrow Interact Switch cap
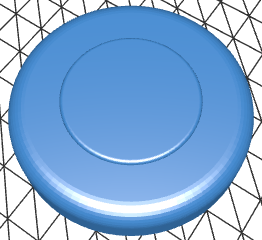
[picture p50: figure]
3D render of circle Interact Switch cap
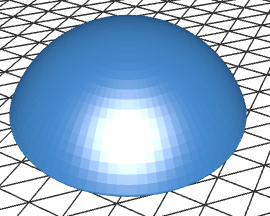
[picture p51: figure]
3D render of domed Interact Switch cap

Arrow | Circle | Dome

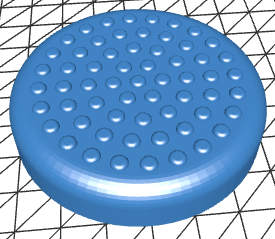
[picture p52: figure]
3D render of Interact Switch cap covered in small dots
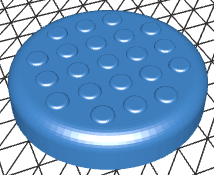
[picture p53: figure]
3D render of Interact Switch cap covered in medium dots
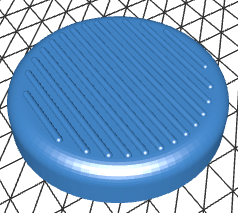
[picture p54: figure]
3D render of Interact Switch cap covered in fine lines

Dots Circles | Dots Wide | Lines

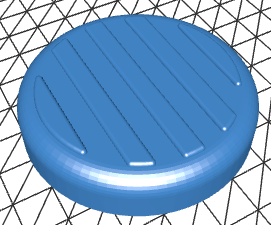
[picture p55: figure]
3D render of Interact Switch cap covered in heavy lines
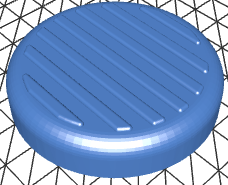
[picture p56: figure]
3D render of Interact Switch cap covered in medium lines
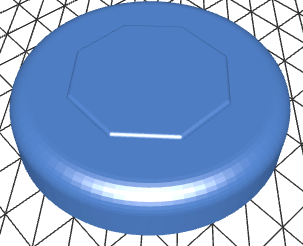
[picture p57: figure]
3D render of Interact Switch cap with an octagon on top

Lines Very Wide | Lines Wide | Octagon

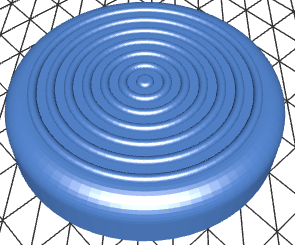
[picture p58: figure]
3D render of Interact Switch cap covered in fine concentric circles
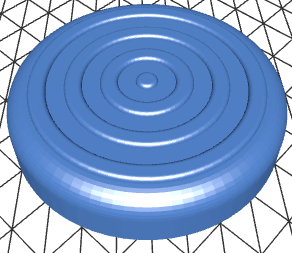
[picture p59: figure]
3D render of Interact Switch cap covered in large concentric circles
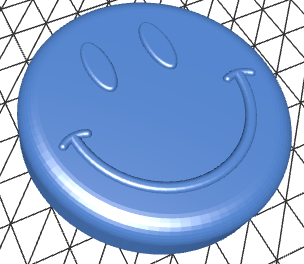
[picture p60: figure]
3D render of Interact Switch cap with a smiley face on top

Rings | Rings Wide | Smile

© 2025 by Neil Squire. This work is licensed under the CC BY SA 4.0 License: http://creativecommons.org/licenses/by-sa/4.0 Files available at https://github.com/makersmakingchange/Interact-Switch Page 1 of 1

V2.0 | July 2025 Interact Switch TOPPER Guide

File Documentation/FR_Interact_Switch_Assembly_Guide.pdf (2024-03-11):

V1.1 | AOÛT 2023

## Commutateur Interactif

## GUIDE DE MONTAGE

BOM 1. 1x socle de commutateur (imprimé en 3D) 2. 1x support de capuchon de bouton (imprimé en 3D) 3. 1x insertion de capuchon de bouton (imprimée en 3D) 4. 1x capuchon de bouton (imprimé en 3D) 5. interrupteur de fin de course Omron SS-3GP 6. 1x câble mono de 3,5 mm 7. 3x vis auto taraudeuses à tête cylindrique M2.5x12 ou no 4, 3/8 po

© 2023 by Neil Squire / Makers Making Change. Le présent ouvrage est placé sous licence CC BY SA 4.0 : http://creativecommons.org/licenses/by-sa/4.0
Les fichiers sont accessibles sur : https://github.com/mwturvey/InteractSwitch (en anglais seulement) | Page 1 of 6

### Required Components

### Outils Requis

- Fer à souder et soudure
- Pince à dénuder
- Tournevis

### Équipement de protection individuelle (ÉPI) requis

- Lunettes de sécurité

### Attribution

La conception du commutateur Interactif de Mike Turvey est utilisée sous licence CC-BY 4.0. Ces instructions ont été adaptées des instructions originales de montage du commutateur Interactif par Mike Turvey, utilisées sous licence CC-BY 4.0. (en anglais seulement)

## GUIDE DE MONTAGE

© 2023 by Neil Squire / Makers Making Change.


Le présent ouvrage est placé sous licence CC BY SA 4.0 : http://creativecommons.org/licenses/by-sa/4.0
Les fichiers sont accessibles sur : https://github.com/mwturvey/InteractSwitch (en anglais seulement) | Page 2 of 6

### GUIDE DE MONTAGE

### Étape 1 - Préparer le câble

Coupez et jetez l’une des fiches du câble audio mono.
Utilisez la pince à dénuder pour retirer soigneusement environ 15 mm de l’isolant extérieur de l’extrémité.

### Étape 2 — Préparer les fils du câble

Enroulez les brins de cuivre pour former un seul fil.

Utilisez la pince à dénuder pour retirer environ 5 mm d’isolant de l’autre fil.

(Remarque : Votre câble peut être différent. Dans le cas où deux fils sont isolés, retirez 5 mm de l’extrémité de chaque fil).

## GUIDE DE MONTAGE

© 2023 by Neil Squire / Makers Making Change.


Le présent ouvrage est placé sous licence CC BY SA 4.0 : http://creativecommons.org/licenses/by-sa/4.0
Les fichiers sont accessibles sur : https://github.com/mwturvey/InteractSwitch (en anglais seulement) | Page 3 of 6

### Étape 3 — Enfiler le câble dans le socle du commutateur

Faites passer le câble dans le trou du socle du
commutateur. Vous ne pourrez pas le faire
après avoir soudé les fils sur l’interrupteur de
fin de course.

### Étape 4 — Souder les fils à l’interrupteur de fin de course

Soudez les fils à l’interrupteur comme illustré
ci-contre.

Remarque : Soudez les deux fils les plus proches du bouton de l’interrupteur.

Autotest : branchez votre interrupteur de fin de cours sur un dispositif activé par commutation puis appuyez sur son bouton.

## GUIDE DE MONTAGE

© 2023 by Neil Squire / Makers Making Change.


Le présent ouvrage est placé sous licence CC BY SA 4.0 : http://creativecommons.org/licenses/by-sa/4.0
Les fichiers sont accessibles sur : https://github.com/mwturvey/InteractSwitch (en anglais seulement) | Page 4 of 6

### Étape 5 — Installer l’interrupteur de fin de course dans le socle

Placez l’interrupteur dans le socle du
commutateur comme illustré ci-contre.

Installez l’interrupteur de sorte que lorsque le câble vient vers vous, son bouton est décalé vers la gauche. Veillez à ce qu’aucun fil ne soit coincé en dessous, empêchant ainsi la sortie complète de l’interrupteur de fin de course.

Enfoncez ensuite le câble dans la fente, comme illustré ci-contre.

### Étape 6 — Assembler le capuchon du bouton

Retournez le capuchon du bouton et introduisez-y son insertion. Si vous n’êtes
pas sûr de la taille à utiliser, commencez
par une insertion de 0,5 mm.

## GUIDE DE MONTAGE

© 2023 by Neil Squire / Makers Making Change.


Le présent ouvrage est placé sous licence CC BY SA 4.0 : http://creativecommons.org/licenses/by-sa/4.0
Les fichiers sont accessibles sur : https://github.com/mwturvey/InteractSwitch (en anglais seulement) | Page 5 of 6

### Étape 7 — Terminer l’assemblage du capuchon de bouton

Insérez le support de capuchon de bouton
dans le capuchon de bouton assemblé.
L’orientation de la partie « ouverte » n’a
pas d’importance.

Remarque : pour une meilleure fluidité du commutateur, poncez les bords du support de capuchon de bouton à l’endroit où il frotte sur celui-ci.

### Étape 8 — Assembler le commutateur

Alignez les trois montants du support de capuchon du commutateur sur les trois trous du socle du commutateur. Fixez le support de capuchon du commutateur au socle du commutateur à l’aide de trois vis.

Remarque : Veillez à ne pas trop serrer les vis. Serrez-les jusqu’à ce que vous remarquiez que la résistance augmente et que le support de capuchon du commutateur est fermement appuyé contre le socle du commutateur.

## GUIDE DE MONTAGE

© 2023 by Neil Squire / Makers Making Change.


Le présent ouvrage est placé sous licence CC BY SA 4.0 : http://creativecommons.org/licenses/by-sa/4.0
Les fichiers sont accessibles sur : https://github.com/mwturvey/InteractSwitch (en anglais seulement) | Page 6 of 6

### Autotest

En dernier lieu, il convient de tester votre commutateur. S’il s’agit de votre premier commutateur, vous aurez probablement besoin de le tester et de déterminer la taille appropriée de l’insertion de capuchon du commutateur.
Lorsque je teste un commutateur, je commence par appuyer plusieurs fois dessus. Tapez-le partout, à plusieurs reprises. Chaque fois que vous appuyez dessus, vous devez entendre un clic lorsqu’il s’enfonce, puis un clic lorsqu’il remonte. Il ne doit jamais rester coincé. Si vous agitez son capuchon, il doit bouger un tant soit peu, sans toutefois donner l’impression de s’entrechoquer. Branchez ensuite le commutateur sur un dispositif activé par commutation pour vous assurer qu’il fonctionne.

### Dépannage

Problème | Solution
Le capuchon du commutateur n’est pas assez serré et s’entrechoque facilement. | Utilisez une insertion de capuchon du commutateur plus grande/épaisse
Le commutateur n’émet aucun bruit lorsqu’il est enfoncé. | Utilisez une insertion de capuchon du commutateur plus petite/plus mince. Une insertion trop grande peut faire en sorte que l’interrupteur de fin de course reste toujours enfoncé. Lorsque c’est le cas, il est fréquent que l’interrupteur de fin de course émette un « clic » en position fermée, lorsque vous vissez le tout ensemble, mais jamais en position ouverte.
Le commutateur reste coincé/ne remonte pas toujours. | Utilisez une insertion de capuchon du commutateur plus petite/plus mince. Une taille plus mince peut suffire à résoudre ce problème.
Le commutateur émet un clic, mais le dispositif activé par commutation ne se met pas en marche. | Branchez le dispositif activé par commutation dans un interrupteur en bon état de marche, simplement pour vous assurer qu’il fonctionne correctement. Vérifiez que la fiche est bien branchée dans le dispositif. Il est possible que la soudure soit endommagée et qu’il faille la refaire. Il se peut que le fil soit rompu à l’intérieur et qu’il faille le remplacer. C’est un point de défaillance particulièrement courant sur les anciens commutateurs.

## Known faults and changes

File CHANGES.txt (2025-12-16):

Version 2.0.2 | 2025-Dec-12
- CAD changes to Button Cap Holder
 - removed edge causing cap to bind.

Version 2.0.1 | 2025-10-28
 - CAD changes to Base
   - increased clearance to better accommodate micro switch
   - added versioning to base
   - increased size of cable hole to 4.2 mm

 - Updated Maker Guide
   - Default insert is 0.6 mm for better fit

 - Updated Build Files
    - Replaced 0.4 mm insert with 0.6 mm insert in main folder.

Version 2.1 | 2025-Aug-31
 - Rebuilt CAD files in one repository
 - Solved a number of issues with poor fits between components
 - Parameterized files to make changes easier
 - Made alternate toppers and inserts derived designs so changes to the base part propagate to all the modified versions 

Version 2.0 | 2025-July-08
 - Documentation was updated using OpenAT documentation standard
 - Changes were made to base and button cap holder to work better with #4 screws, but makes them no longer compatible with M2.5 screws.
 - Changes were made to the plain cap to improve printing on the top face

Version 1.1 | 2023-Sep-30
 - CAD design was recreated in Fusion 360

Version 1.0 | 2020-mmm-DD
 - Initial Design by Michael Turvey, CC-BY

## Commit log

2023-10-30 Added assembly guides
2024-03-11 Updated assembly guide - fixed typo and added graphic
2025-02-24 Reorganize repository
    [ButtonBase.SLDPRT, ButtonBase_Spade.SLDPRT, ButtonBase_Spade.STL, ButtonCapHolder.SLDPRT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]
2025-05-09 Updated Base
    Increased clearance of holes on base so screw can spin freely, changed design of screw holes to allow them to print better with no supports, and changed the hole depth slightly to better accommodate 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
    [Interact_Switch_Base.f3d, Interact_Switch_Base.stl]
2025-05-09 Updated screw holes
    Made screw holes wider from 2mm to 2.4mm to lower the force required to screw them into place, and added a chamfer to make it easier to start a screw in the hole
    [Interact_Switch_Holder.f3d, Interact_Switch_Holder.stl, Quick Fix ButtonCapHolder v3.f3d]
2025-05-09 Plain cap print improvements
    Changed design of plain cap slightly to make bridging easier when printed face down
    [Interact_Switch_Cap_Plain.STL, Interact_Switch_Cap_Plain.f3d, Interact_Switch_Cap_Plain.step]
2025-07-08 Updated documentation
    Updated documentation to OpenAT documentation template standards
    [Interact_Switch_BOM.csv, Interact_Switch_BOM.xlsx]
2025-09-03 Updated CAD and STL files
    Changed the CAD and STL files to the new unified Interact fusion file
    [ButtonBase.SLDPRT, ButtonBase_Spade.SLDPRT, ButtonCapHolder.SLDPRT, ButtonCapInsert_0.2mm.SLDPRT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]
2025-09-22 Added soldering jig files and documentation
    [Interact_Switch_Solder_Jig.stl, Switch Soldering Jig.f3z]
2025-10-07 Update Interact_Switch_Insert_0.4mm.stl
    Flipped the orientation for printing
    [Interact_Switch_Insert_0.4mm.stl]
2025-10-16 Increased cable clearance
    [Interact Switch.f3z, Interact_Switch_BOM.xlsx, Interact_Switch_Base.stl]
2025-10-23 Updated the fit of the switch
    Updated the switch holder on the base to better fit the switch, and changed the default insert to 0.6mm
    [Interact Switch.f3z, Interact_Switch_Base.stl, Interact_Switch_Insert_0.4mm.stl, Interact_Switch_Insert_0.6mm.stl]
2025-10-28 Clean-up print files
    Remove old, obsolete base variant
    Rename and move cap and insert options.
    [ButtonBase_Spade.STL, ButtonCapInsert_0.2mm.STL, ButtonCapInsert_0.3mm.STL, ButtonCapInsert_0.4mm.STL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]
2025-10-31 Updated base and fusion file
    Updated base and fusion file as per comments on merge request
    [Interact Switch.f3z, Interact_Switch_Base.stl]
2025-12-16 Fixed issue where cap holder was getting caught
    [Interact Switch.f3z, Interact_Switch_Holder.stl]
